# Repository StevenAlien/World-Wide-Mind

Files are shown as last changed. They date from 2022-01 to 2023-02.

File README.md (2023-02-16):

# World-Wide-Mind
Ultra-low cost single channel EEG decoding device with Espressif ESP32 running MicroPython

Conference Paper: <a href="https://doi.org/10.1109/EMBC48229.2022.9871064">Development of an Ultra Low-Cost SSVEP-based BCI Device for Real-Time On-Device Decoding</a>

Preprint: <a href="https://doi.org/10.1101/2022.01.29.478203">Development of an Ultra Low-Cost SSVEP-based BCI Device for Real-Time On-Device Decoding</a>

The code can be found <a href="https://github.com/JamesTev/EEG-decoding/">here</a>.

Project details can be found <a href="https://www.imperial.ac.uk/next-generation-neural-interfaces/resources/eeg/">here</a>.

This work is released under the 
<a href="http://creativecommons.org/licenses/by-sa/4.0/">Creative Commons Attribution-ShareAlike 4.0 International license</a>.

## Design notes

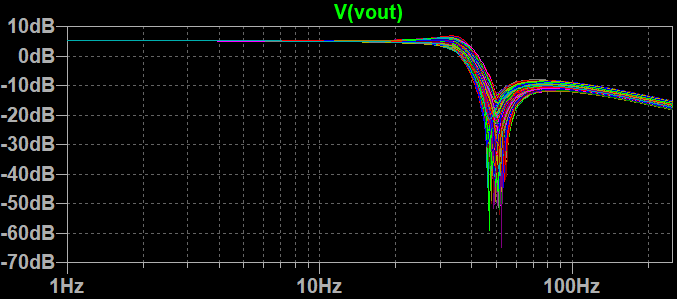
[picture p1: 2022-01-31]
LTspice/Hourglass_Mag_vs_Freq.PNG

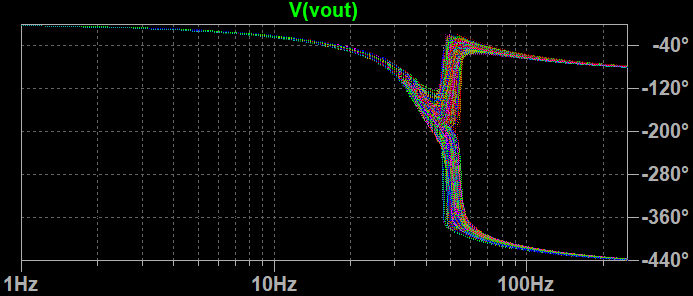
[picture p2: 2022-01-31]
LTspice/Hourglass_Phase_vs_Freq.PNG

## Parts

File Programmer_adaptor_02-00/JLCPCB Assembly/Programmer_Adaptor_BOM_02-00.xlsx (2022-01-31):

Comment | Designator | Footprint | LCSC Part #
100nF | C1 | 0402 | C1525
4.7uF | C5 | 0402 | C23733
100nF | C6 | 0402 | C1525
1uF | C10 | 0402 | C52923
100nF | C11 | 0402 | C1525
4.7uF | C12 | 0402 | C23733
100nF | C13 | 0402 | C1525
100nF | C17 | 0402 | C1525
19-217/GHC-YR1S2/3T | D1 | LED_0603 | C72043
SP3010-04UTG | D2 | uDFN-10_1.0x2.5x0.5P | C151304
SP3010-04UTG | D3 | uDFN-10_1.0x2.5x0.5P | C151304
SML-LX0603IW-TR | D10 | LED_0603 | C2286
FCI-10118193-0001LF | J1
Mill-Max 827-22-006-10-001101 | J2
SS8050-G | Q1 | SOT-23-3 | C164886
SS8050-G | Q2 | SOT-23-3 | C164886
10kohm | R1 | 0402 | C25744
0ohm | R2 | 0402 | C17168
0ohm | R3 | 0402 | C17168
10kohm | R5 | 0402 | C25744
10kohm | R6 | 0402 | C25744
4.7kohm | R8 | 0402 | C25900
1kohm | R30 | 0402 | C11702
1kohm | R31 | 0402 | C11702
Solder Bridge 0402 | SB1
Solder Bridge 0402 | SB2
TS-1185-C-A-A-A | SW1 | SW-SMD-2_3.0x4.0x1.7 | C561518
TS-1185-C-A-A-A | SW2 | SW-SMD-2_3.0x4.0x1.7 | C561518
Keystone Electronics 5002 | TP1
Keystone Electronics 5002 | TP2
Keystone Electronics 5002 | TP3
Keystone Electronics 5002 | TP4
Keystone Electronics 5002 | TP5
Keystone Electronics 5002 | TP6
CP2102-GMR | U2 | MLP | C6568

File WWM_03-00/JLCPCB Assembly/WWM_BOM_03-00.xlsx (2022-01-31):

Comment | Designator | Footprint | LCSC Part #
100 nF | C1 | 0402 | C1525
22 uF | C2 | 0603 | C59461
100 nF | C3 | 0402 | C1525
6pF | C4 | 0402 | C30274
22 uF | C5 | 0603 | C59461
100 nF | C6 | 0402 | C1525
100 nF | C7 | 0402 | C1525
100 nF | C8 | 0402 | C1525
100 nF | C9 | 0402 | C1525
100 nF | C10 | 0402 | C1525
100 nF | C11 | 0402 | C1525
100 nF | C12 | 0402 | C1525
1.5nF | C13 | 0402 | C23967
470nF | C14 | 0402 | C47339
330nF | C15 | 0402 | C307420
4.7uF | C16 | 0402 | C23733
1 uF | C17 | 0402 | C52923
68nF | C18 | 0402 | C12529
3.3nF | C19 | 0402 | C26404
4.7uF | C20 | 0402 | C23733
1u F | C21 | 0402 | C52923
100 nF | C22 | 0402 | C1525
100 nF | C23 | 0402 | C1525
100 nF | C24 | 0402 | C1525
330nF | C25 | 0402 | C307420
68nF | C26 | 0402 | C12529
47nF | C27 | 0402 | C26403
220pF | C28 | 0402 | C1530
220pF | C29 | 0402 | C1530
100 nF | C30 | 0402 | C1525
150pF | C31 | 0402 | C1527
10 uF | C32 | 0402 | C15525
100 nF | C33 | 0402 | C1525
100 nF | C34 | 0402 | C1525
1u F | C35 | 0402 | C52923
100 nF | C36 | 0402 | C1525
LESD8D3.3CT5G | D1 | SOD-882 | C172410
LESD8D3.3CT5G | D2 | SOD-882 | C172410
LESD8D3.3CT5G | D3 | SOD-882 | C172410
LESD8D3.3CT5G | D4 | SOD-882 | C172410
LESD8D3.3CT5G | D5 | SOD-882 | C172410
LESD8D3.3CT5G | D6 | SOD-882 | C172410
LESD8D3.3CT5G | D7 | SOD-882 | C172410
LESD8D3.3CT5G | D8 | SOD-882 | C172410
LESD8D3.3CT5G | D9 | SOD-882 | C172410
LESD8D3.3CT5G | D10 | SOD-882 | C172410
19-217/GHC-YR1S2/3T | D11 | LED_0603 | C72043
KT-0603R | D12 | LED_0603 | C2286
GZ2012D601TF | FB1 | 0805 | C1017
Laird MGV252012S2R2M-10 | L1 | SMD_2.5x2.0x1.2mm | C375952
10kO | R1 | 0402 | C25744
88.7kO | R2 | 0402 | C25922
510kO | R3 | 0402 | C11616
10kO | R5 | 0402 | C25744
100.0 O | R6 | 0402 | C25076
24kO | R7 | 0402 | C25769
1kO | R8 | 0402 | C11702
24kO | R9 | 0402 | C25769
200kO | R10 | 0402 | C25764
100kO | R11 | 0402 | C25741
100kO | R12 | 0402 | C25741
100kO | R13 | 0402 | C25741
6.8kO | R14 | 0402 | C25917
16kO | R15 | 0402 | C25759
11kO | R16 | 0402 | C25749
100kO | R17 | 0402 | C25741
20kO | R18 | 0402 | C25765
330kO | R19 | 0402 | C25778
10kO | R20 | 0402 | C25744
8.2kO | R21 | 0402 | C25924
10kO | R22 | 0402 | C25744
330kO | R24 | 0402 | C25778
200kO | R25 | 0402 | C25764
10kO | R27 | 0402 | C25744
0.0 O | R28 | 0402 | C17168
71.5 O | R29 | 0603 | C23104
1MO | R31 | 0402 | C26083
0.0 O | R32 | 0402 | C17168
0.0 O | R33 | 0402 | C17168
680kO | R34 | 0603 | C25822
1MO | R35 | 0402 | C26083
220.0 O | R36 | 0402 | C25091
1kO | R37 | 0402 | C11702
Leader Tech SMS-403C | SH1
TS-1185-C-A-A-A | SW1 | SW-SMD-2_3.0x4.0x1.7 | C561518
TS-1185-C-A-A-A | SW2 | SW-SMD-2_3.0x4.0x1.7 | C561518
Espressif Systems ESP32-WROOM-32E | U1 | QFN-38_EP_18.0x25.5x1.27P | C701341
TPS63000DRCRG4 | U2 | SON-10_EP_3.0x3.0x0.5P | C24966
LM66100DCKR | U3
AD5160BRJZ10-RL7 | U4 | SOT-23 | C40097
REF1933AIDDCT | U5 | TSOT-23-5, SOT-23-5
MCP6002T-I/SN | U6 | SOIC | C7377
INA126EA/2K5 | U7 | MSOP
MCP6002T-I/SN | U9 | SOIC | C7377
MCP6002T-I/SN | U10 | SOIC | C7377

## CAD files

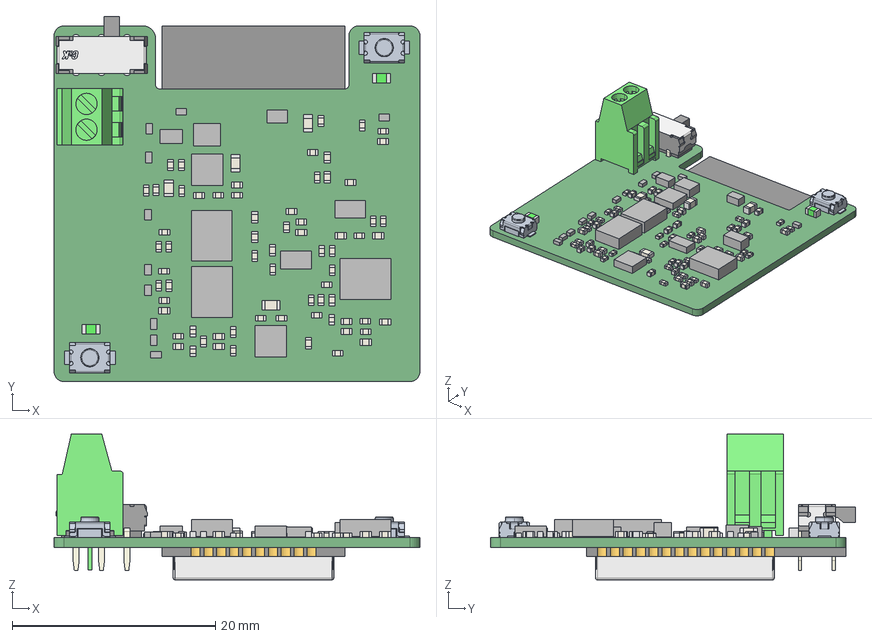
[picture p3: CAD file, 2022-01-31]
WWM_03-00/WWM_03-00.step
36.0 x 35.9 x 14.4 mm
Extruded x 242
c-282834-2-c-3d_RGB3394611
ts-1185-c-a-a-a x 2
JS202011AQN
pcb
pads
antenna
logo

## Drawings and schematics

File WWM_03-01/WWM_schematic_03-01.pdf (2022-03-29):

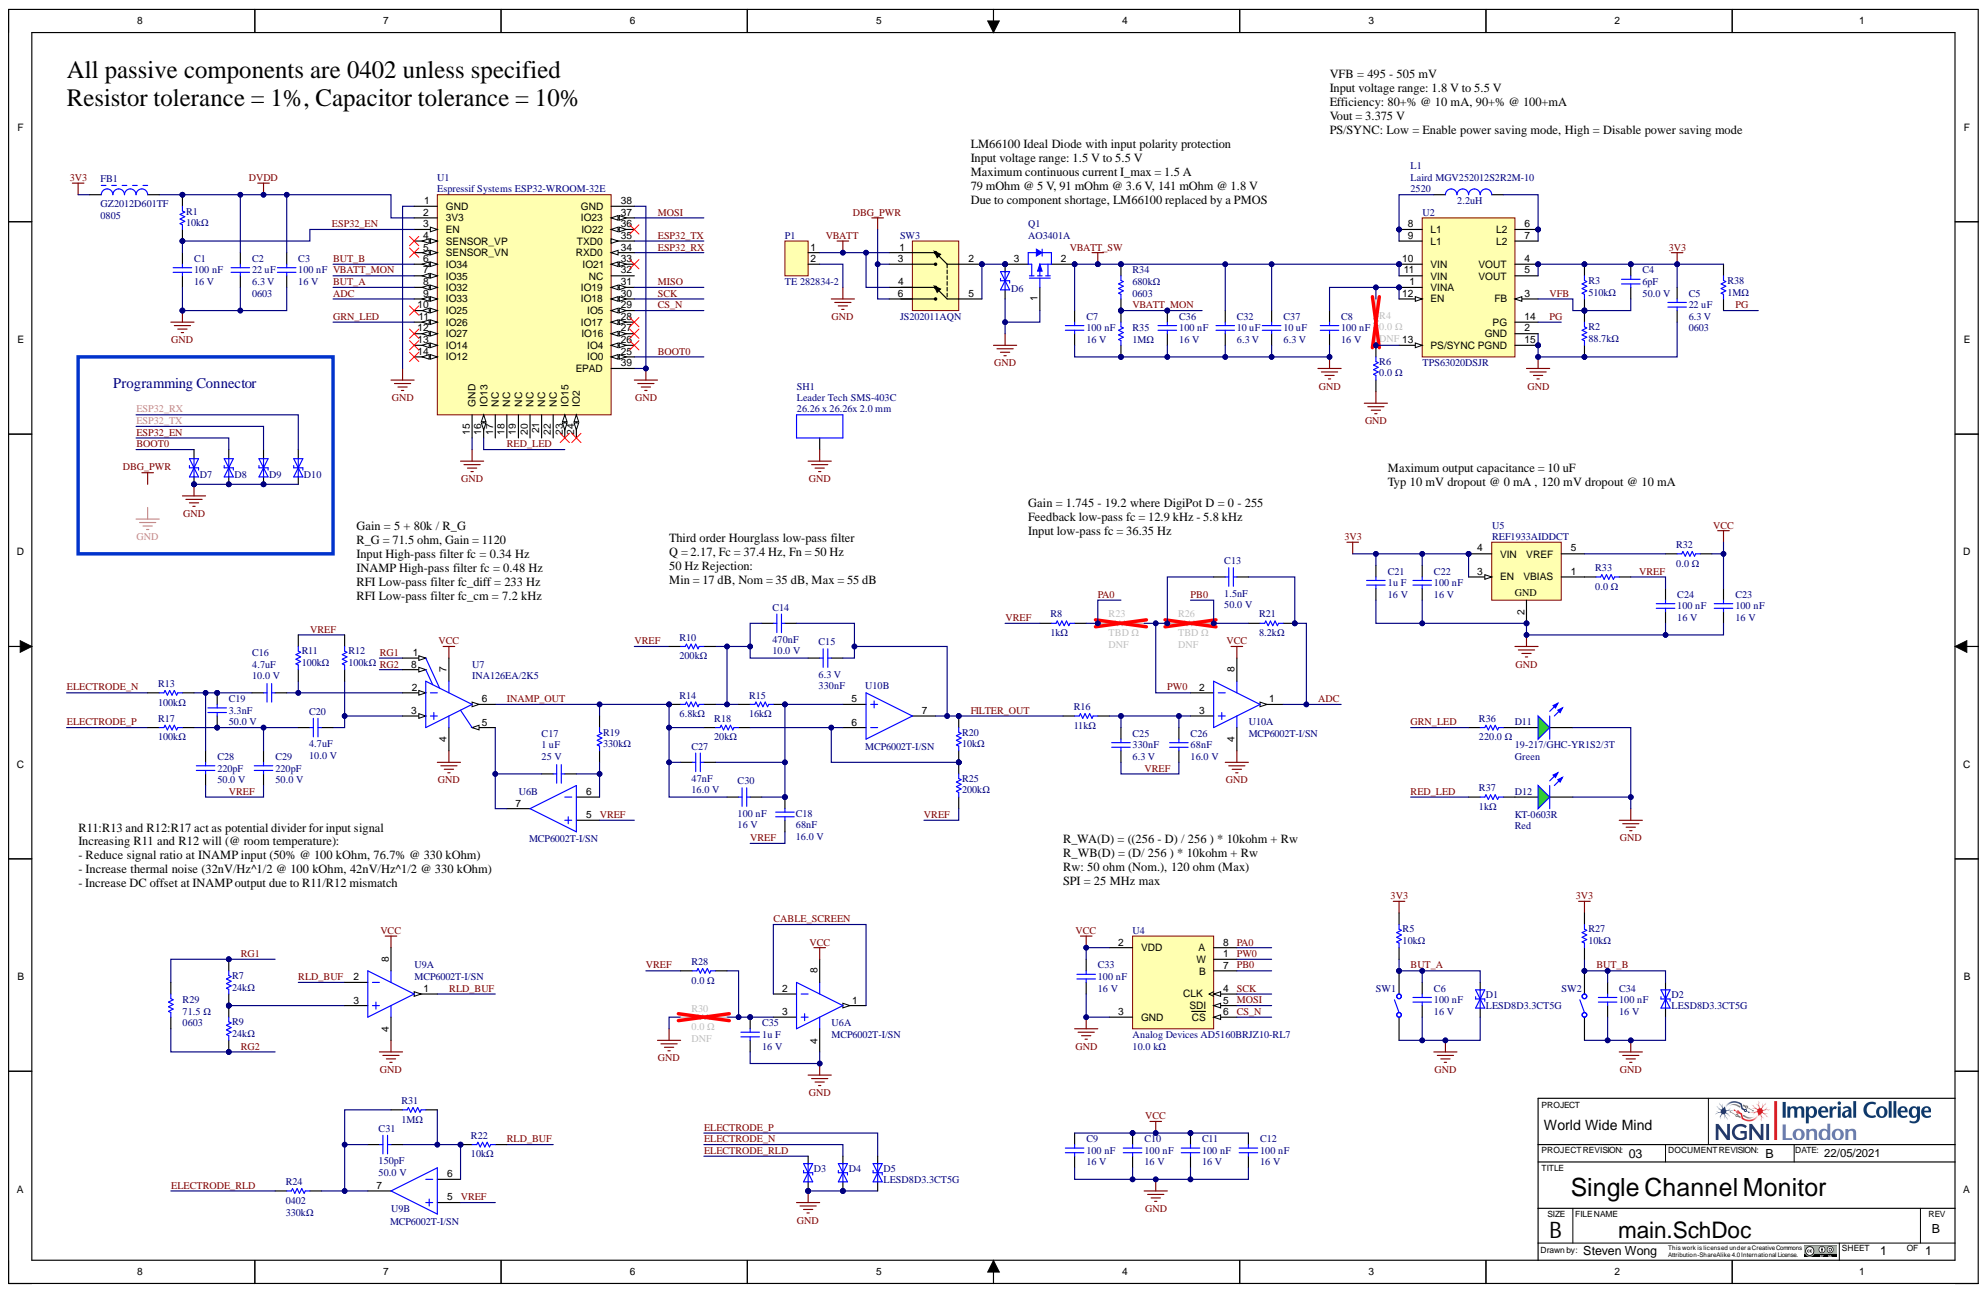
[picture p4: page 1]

All passive components are 0402 unless specified
Resistor tolerance = 1%, Capacitor tolerance = 10%

VFB = 495 - 505 mV
Input voltage range: 1.8 V to 5.5 V
Efficiency: 80+% @ 10 mA, 90+% @ 100+mA
Vout = 3.375 V
PS/SYNC: Low = Enable power saving mode, High = Disable power saving mode

LM66100 Ideal Diode with input polarity protection
Input voltage range: 1.5 V to 5.5 V
Maximum continuous current I_max = 1.5 A
79 mOhm @ 5 V, 91 mOhm @ 3.6 V, 141 mOhm @ 1.8 V
Due to component shortage, LM66100 replaced by a PMOS

Typ 10 mV dropout @ 0 mA , 120 mV dropout @ 10 mA

Gain = 1.745 - 19.2 where DigiPot D = 0 - 255
Feedback low-pass fc = 12.9 kHz - 5.8 kHz

Input low-pass fc = 36.35 Hz Gain = 5 + 80k / R_G
R_G = 71.5 ohm, Gain = 1120
Input High-pass filter fc = 0.34 Hz
INAMP High-pass filter fc = 0.48 Hz
RFI Low-pass filter fc_diff = 233 Hz
RFI Low-pass filter fc_cm = 7.2 kHz

Third order Hourglass low-pass filter
50 Hz Rejection:
Min = 17 dB, Nom = 35 dB, Max = 55 dB

R11:R13 and R12:R17 act as potential divider for input signal
Increasing R11 and R12 will (@ room temperature):
- Reduce signal ratio at INAMP input (50% @ 100 kOhm, 76.7% @ 330 kOhm)
- Increase thermal noise (32nV/Hz^1/2 @ 100 kOhm, 42nV/Hz^1/2 @ 330 kOhm)
- Increase DC offset at INAMP output due to R11/R12 mismatch

R_WA(D) = ((256 - D) / 256 ) * 10kohm + Rw
R_WB(D) = (D/ 256 ) * 10kohm + Rw
Rw: 50 ohm (Nom.), 120 ohm (Max)
SPI = 25 MHz max

PROJECT World Wide Mind

Drawn by: Steven Wong

This work is licensed under a Creative Commons
Attribution-ShareAlike 4.0 International License.

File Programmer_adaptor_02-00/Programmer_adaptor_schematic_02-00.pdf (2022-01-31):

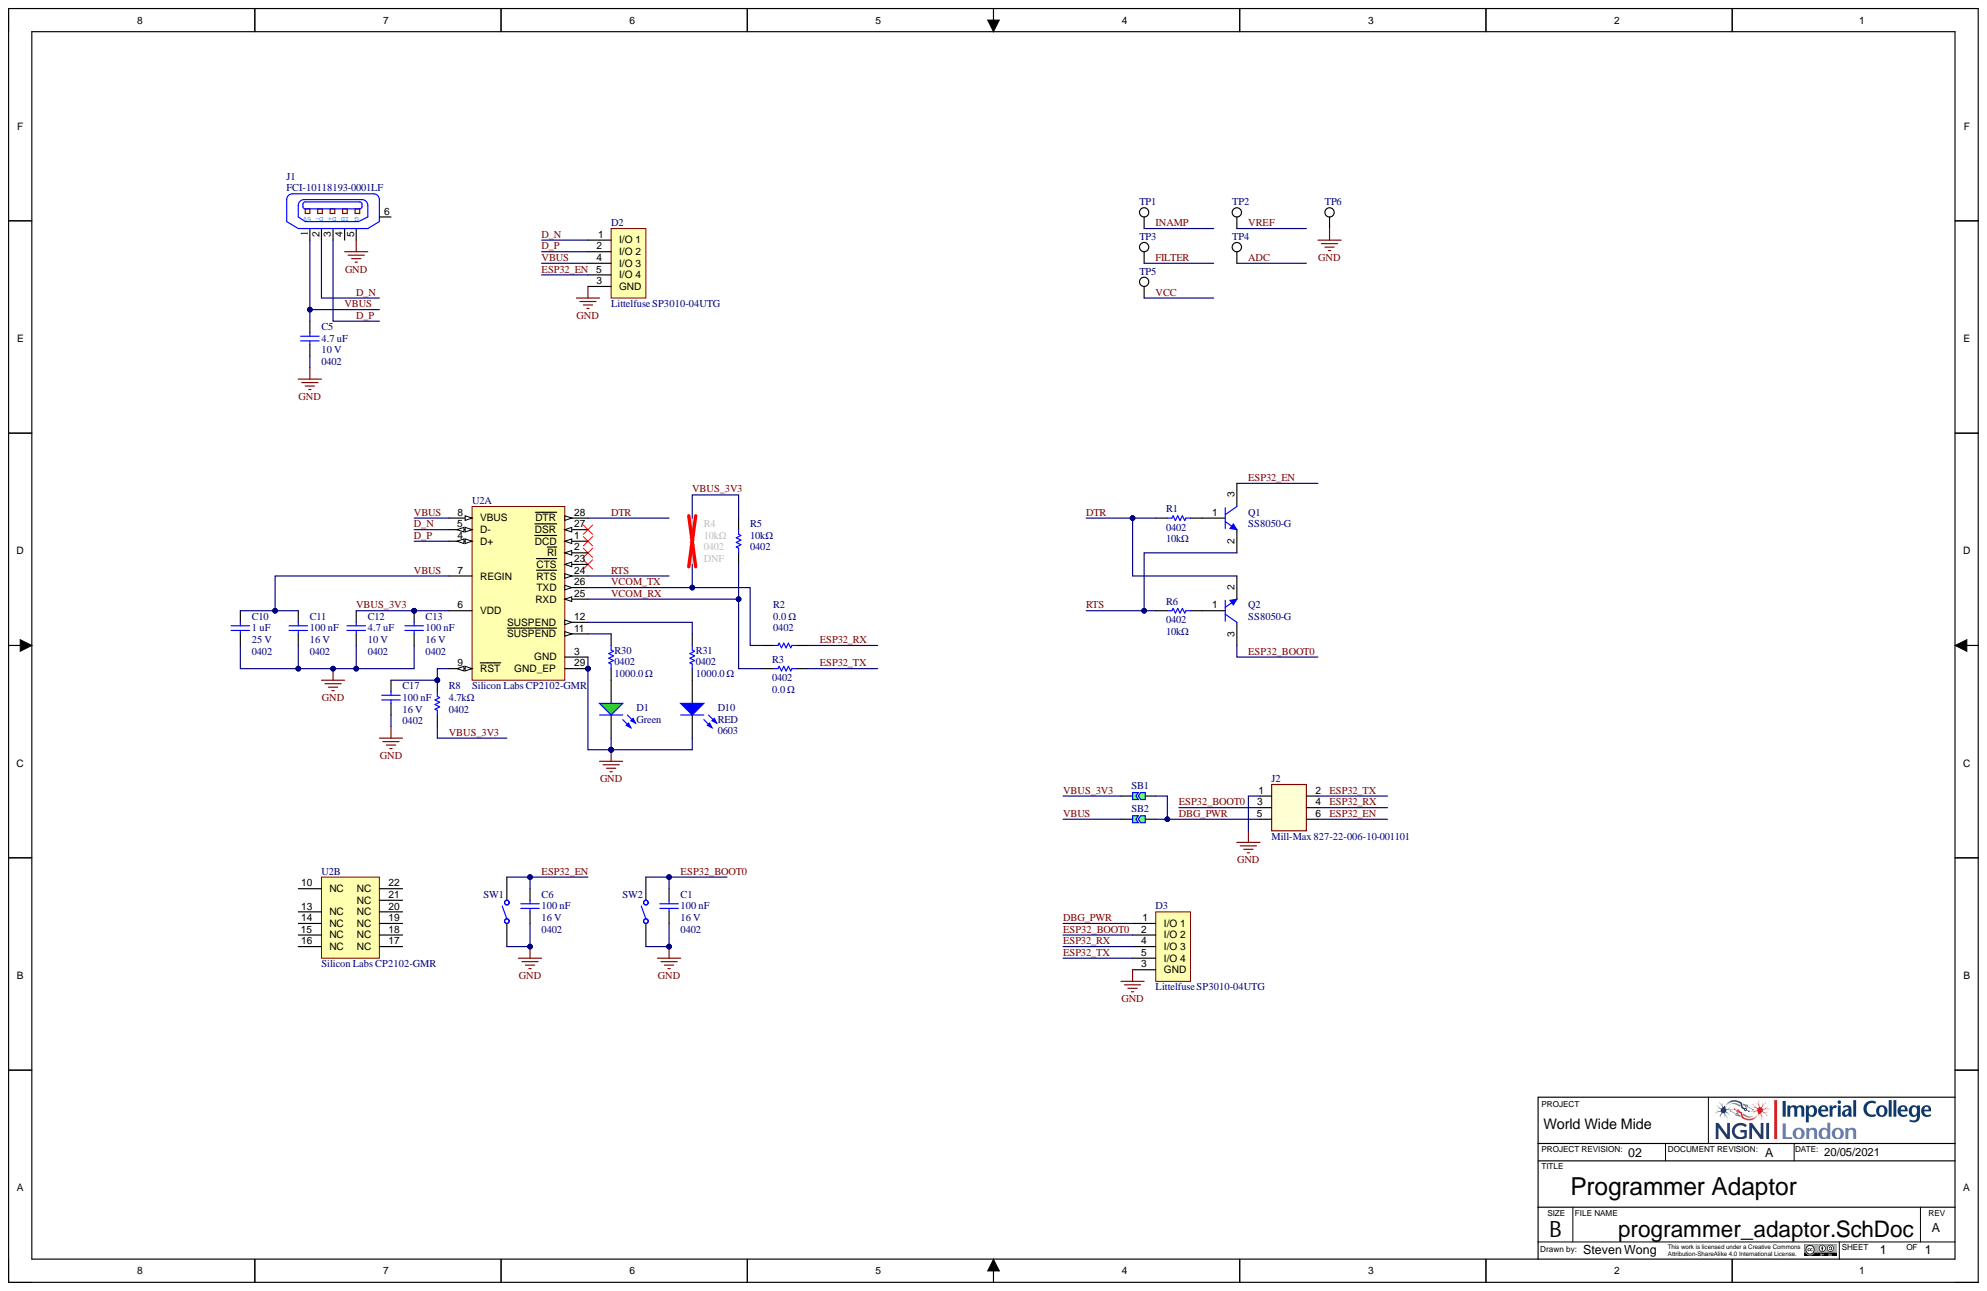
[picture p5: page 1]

VBUS_3V3 | | VDD 6 | VCOM_TX

VCOM_RX

PROJECT World Wide Mide

DOCUMENT REVISION: A | DATE: 02 20/05/2021 PROJECT REVISION:

SIZE | FILE NAME | REV A

Drawn by: Steven Wong This work is licensed under a Creative Commons Attribution-ShareAlike 4.0 International License. | SHEET OF

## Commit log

2022-01-30 Schematic uploaded
    Currently written "© Copyright, all rights reserved". The licencing will be changed to Creative Commons Attribution-ShareAlike 4.0 International license and align to the Github project.
2022-01-31 Design files uploaded
    Files re-organised. Altium design files, ODB++ files, Gerber files and JLCPCB assembly related files added.
    [Programmer Adaptor.PrjPcb, Programmer_Adaptor_BOM_02-00.xlsx, Programmer_Adaptor_Pick_Place_02-00.csv, Single Channel Monitor.PrjPcb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]
2022-03-29 Added WWM_03-01 Layout
    Added WWM_03-01 layout file and updated WWM_03-01 schematic with red cross over not fitted components
    [Single Channel Monitor.PrjPcb, main.PcbDoc]
